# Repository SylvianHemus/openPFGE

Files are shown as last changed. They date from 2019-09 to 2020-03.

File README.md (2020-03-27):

# openPFGE

Open source and low cost pulsed-field gel electrophoresis [PFGE] equipment.
<details>
  <summary>Intro | Description | Results | Costs</summary>

## Intro
Biochemistry - including biotechnology, molecular biology, protein engineering, among others - is an area were high sophisticated equipment is required. In general, just a few equipment have an open source version - i.e. PCR - and, because of low offerer number, costs of these equipment tent to be overpriced, limiting it access to many research centers or labs.

## Description
Pulsed-field gel electrophoresis [PFGE] is a technique that allows the separation of very large DNA molecules - up to ~10 Mbp, in contrast of up to ~50 Kbp of normal electrophoresis - by a periodic change in the direction of the electric field, widely used in many biochemistry labs. This work considers the design and construction of a open source and low cost PFGE, implementing a Rotating Gel Electrophoresis (RGE). The design considers the use of a standard commercially available electrophoresis chamber and the construction of an agarose gel rotation system using 3D printed parts, a servo motor and simple electronics.

In order to keep the design simple and low cost as possible, a gel rotation system inside a standard large electrophoresis chamber was designed to achieve the electric field direction change of the PFGE. The gel rotation system considers simple 3D printed parts composed of: a tray, that supports the gel; a tray cover, that fixes the gel position; a stem, that goes from the tray cover through the electrophoresis chamber cover and joins the servo motor; and, a joint, of the stem to the servo motor that allows easy release of the tray. It also considers a 180 degrees, 5 [V], high speed and accuracy digital servo motor that allows the PFGE to move at any angle.

The buffer cooling system is composed of a small 12V pump that circulates the buffer through a peltier cooler elements based refrigeration system. A NTC epoxy thermistor temperature sensor provides the capacity to retrieve the current buffer temperature in order to feedback the cooling system.

The circuit is driven by an Arduino Nano microprocessor. It holds a serial OLED module to display the parameters of the electrophoresis run independent from the smartphone. Fans and the pump are controlled by digital outputs through high current MOSFETs. It considers a Bluetooth module to provide communication to a smartphone for system control.

## Results & costs
The equipment is capable of the separation of DNA molecules up to ~2 Mbp [See *Fig 1*] with the same protocols as commercial equipment. A 10 Mpb marker is about to be tested. It costs USD ~$500, about 1/50 of the price of commercial equipment, considering the chamber and the power source. All coding, electronics, 3D parts and documentation is public available on GitLab.
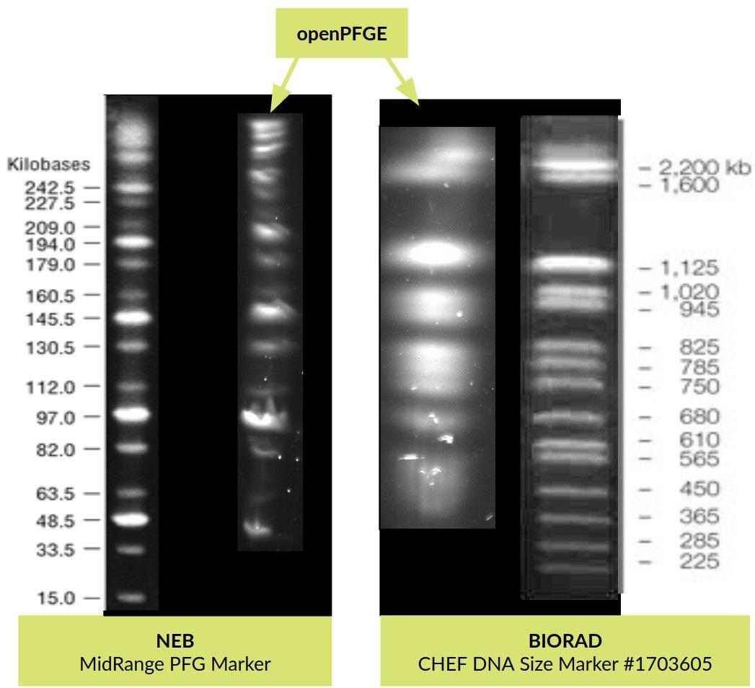
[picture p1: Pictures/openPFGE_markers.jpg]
Two commercial markers separated by openPFGE in contrast to references

**Fig. 1 |** Two commercial markers separated by openPFGE in contrast to references<br/><br/>
</details>

# Fabrication and assembly

1. Aquire all components listed in the hardware part list section
2. Print all parts in the last folder of *3D printing* folder using PLA at 0.25mm layer height, except for *pin.FCStd* that had 0.1mm layer height. See *Pictures/Gel_tray.jpg* and *Pictures/Servo_motor_support_and_join.jpg* to see how they look like in the final assembly.
3. Using some strong glue, put the magnets in the *motor joint* part as shown in *Pictures/Magnets_motor_joint.jpg* and in the *tray cover joint* part
4. Using some fishing line build the gel tray as shown in *Pictures/Gel_tray.jpg*
5. Fabricate the circuit PCB using the last version of the *fzz* file in the *Circuit* folder. You can find a good price and service at [AISLER](https://aisler.net/)
6. Assemble the circuit by soldering the parts to the PCB. The PCB has the description of the components on its skilscreen. A picture of the PCB assembly is at *Circuit/Pictures/Circuit_assembly.jpg*.
7. Assemble the servo motor to its printed support. Attach the *motor joint* to the servo arm.
8. Power the 12V power source to the circuit
9. Download [the Android app](https://play.google.com/store/apps/details?id=cl.paralelos.openpfge)
10. Turn on the circuit switch and start your electrphoresis

# Hardware parts list
## Gel rotating system
### Electrophoresis chamber
Design of motor support was made based on [BT103](https://www.btlabsystems.com/Agarose_Electrophoresis_BT103) electrophoresis chamber:

- Gel Dimension: 60 x 60, 120 x 60, 60 x 120, 120 x 120mm
- Number of samples: 6, 8, 11, 13, 18, 25
- Comb thickness: 1.0, 1.5 & 2.0mm
- Buffer volume: 650ml

### Servo
- Digital servo DS3218 [like this one](https://aliexpress.com/item/1943129663.html)
- Print 1 X *motor joint.FCStd*
- Print 1 X *motor support.FCStd*
- 4 X 3mm diameter / >10 mm length screw-nut to fix the servo to the *motor joint*
- 1 X 3mm diameter / 6 mm length screw-nut to fix the servo to the *motor support*
- 1 X 3mm diameter / 12 mm length screw-nut to fix the servo to the *motor support*
- 2 X 7mm diameter / 5 mm height N35 magnet [like this one](https://aliexpress.com/item/32277590868.html)

### Gel tray
- Print 2 X *pin.FCStd*
- Print 1 X *tray.FCStd*
- Print 1 X *tray cover.FCStd*
- Print 1 X *tray cover joint.FCStd*
- 2 X 7mm diameter / 5 mm height N35 magnet [like this one](https://aliexpress.com/item/32277590868.html)
- 30 cm fishing line

### Refigeration system
- Peristaltic Pump 12V [like this one](https://aliexpress.com/item/32882495060.html)
- Peltier cooler 12V [like this one](https://aliexpress.com/item/33028954404.html)

## Circuit parts list

### Microcontroller
Arduino Nano v3.0 ATMEGA328P [like this one](https://aliexpress.com/item/32824272738.html)

### Bluetooth
HC-05  [like this one](https://aliexpress.com/item/32953559442.html)

### Power
- L7805CV Transistor voltage regulator (1.5 A) with a heat disipator
- 100 uF capacitor
- 10 uF capacitor
- Diode 1A [like this one](https://components101.com/1n4007-diode)
- 12V / 30 A power source [like this one](https://aliexpress.com/item/32917708245.html)
- Power switch

### LCD
LCD I2C 16x2 [like this one](https://aliexpress.com/item/32786773241.html)

### Refigeration
- 1 X Epoxy NTC thermistor temperature sensor 10K 1% [like this one](https://aliexpress.com/item/32654331022.html)
- 3 X Diode 1A [like this one](https://components101.com/1n4007-diode)
- 5 X IRLB8743PBF MOSFET [like this one](https://www.infineon.com/dgdl/irlb8743pbf.pdf?fileId=5546d462533600a4015356605d6b2593)
- 6 X 10K resistor

### Input / Output
- 8 X Screw Terminal / 3.5mm / 2 pins
- 1 X Screw Terminal / 3.5mm / 3 pins

# Android APP
Available at [Google play](https://play.google.com/store/apps/details?id=cl.paralelos.openpfge).
Source code available at *App Android* folder.

# License

- Hardware license: CERN Open Hardware License 1.2
- Software license: GPL v3
- Documentation license: CC BY 4.0 International

# Open hardware certification

[OSHW] CL000001 | Certified open source hardware | [oshwa.org/cert](oshwa.org/cert)

# Thanks to
## 3D printing
[Fablab U. de Chile](http://fablab.uchile.cl/)
## App
Item picker [link](https://gist.github.com/kristopherjohnson/660656bb9e18e23146c0)
## Firmware
Thermistor code [link](https://learn.adafruit.com/thermistor/using-a-thermistor)
ArduinoJson [link](https://arduinojson.org/)
## Logo
Based on logo by [link](https://www.instagram.com/rubenferlodotcom/)

# Contact
Fell free to write about any questions to [diego.lagos.s@ug.uchile.cl](mailto:diego.lagos.s@ug.uchile.cl)

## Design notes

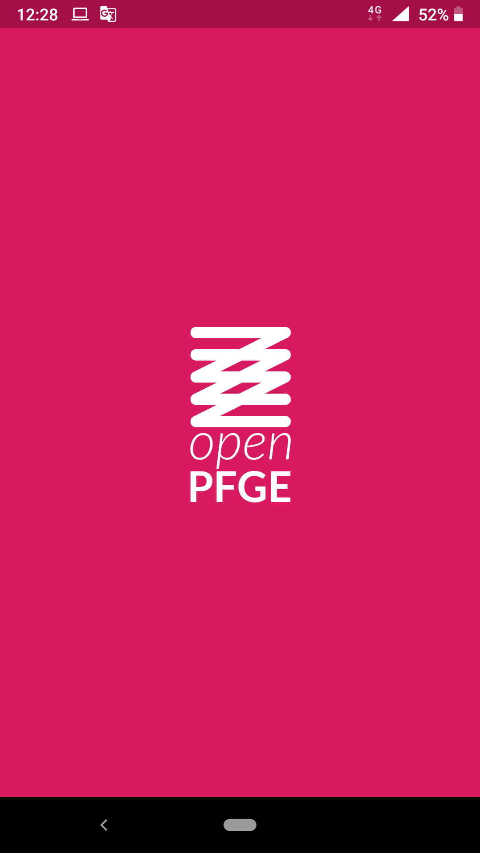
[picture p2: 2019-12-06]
App Android/Pictures/Screenshot_20191121-122839.png

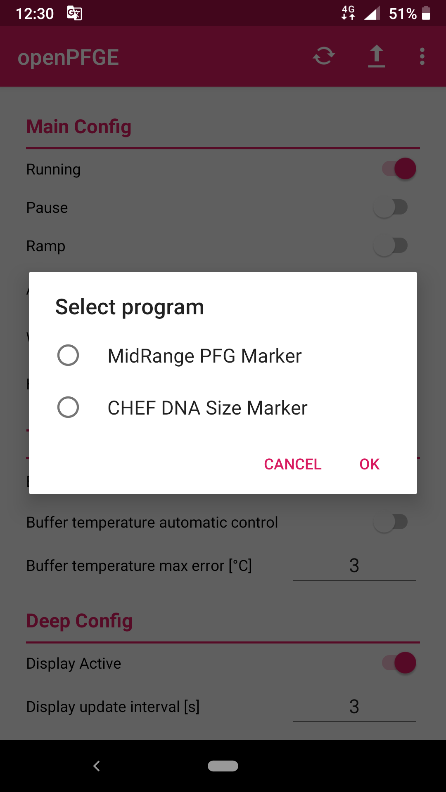
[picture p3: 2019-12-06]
App Android/Pictures/Screenshot_20191121-123048.png

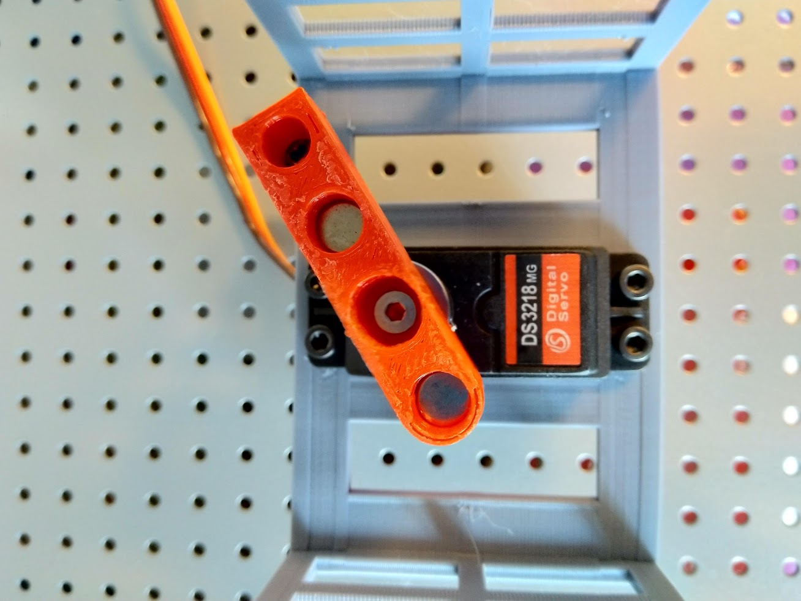
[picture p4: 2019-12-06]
Pictures/Magnets_motor_joint.jpg

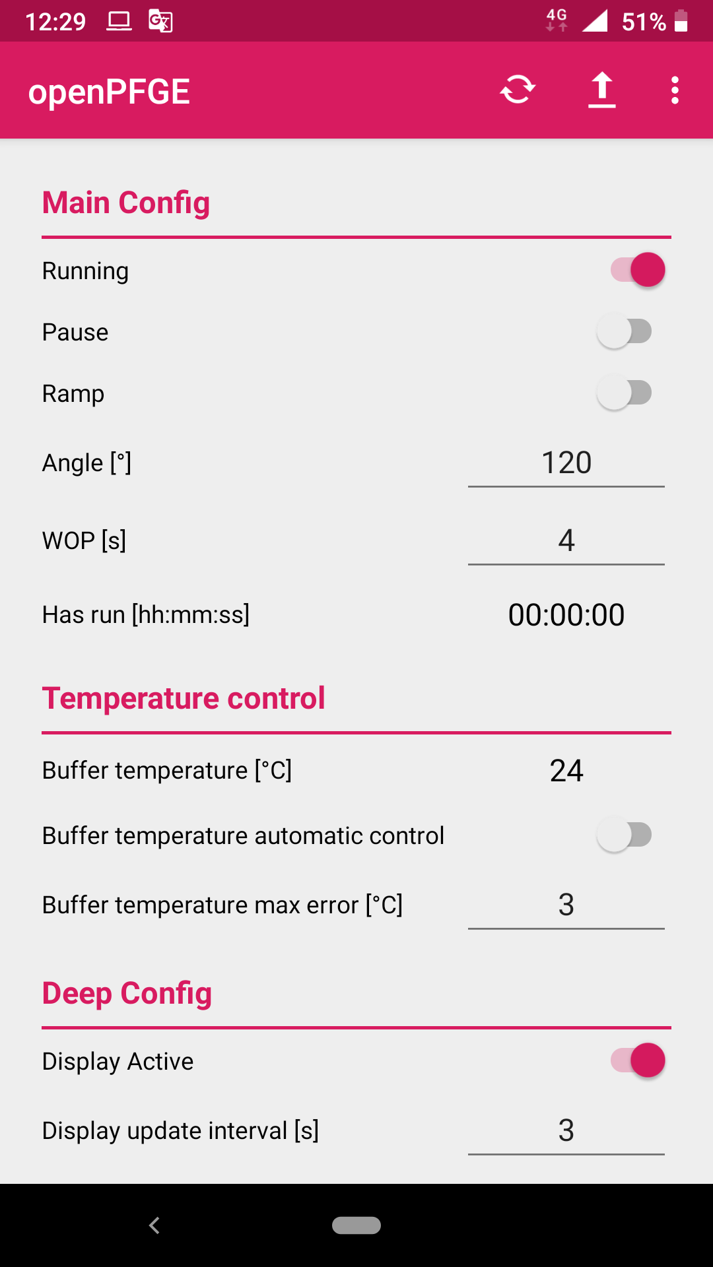
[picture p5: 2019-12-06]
App Android/Pictures/Screenshot_20191121-122949.png

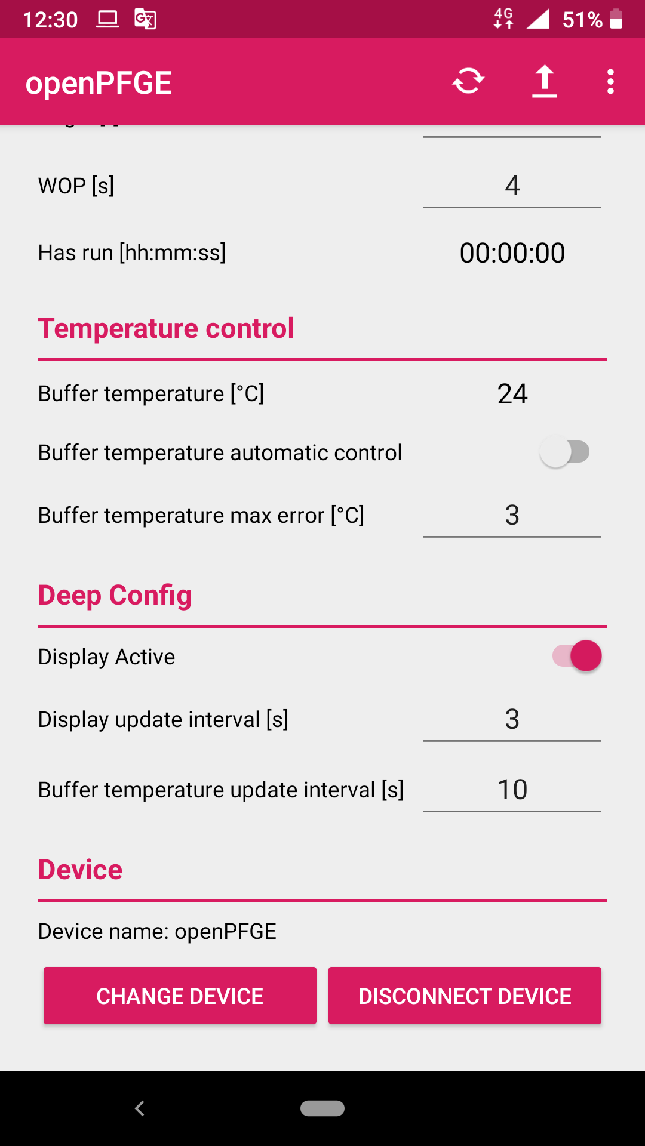
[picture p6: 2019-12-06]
App Android/Pictures/Screenshot_20191121-123005.png

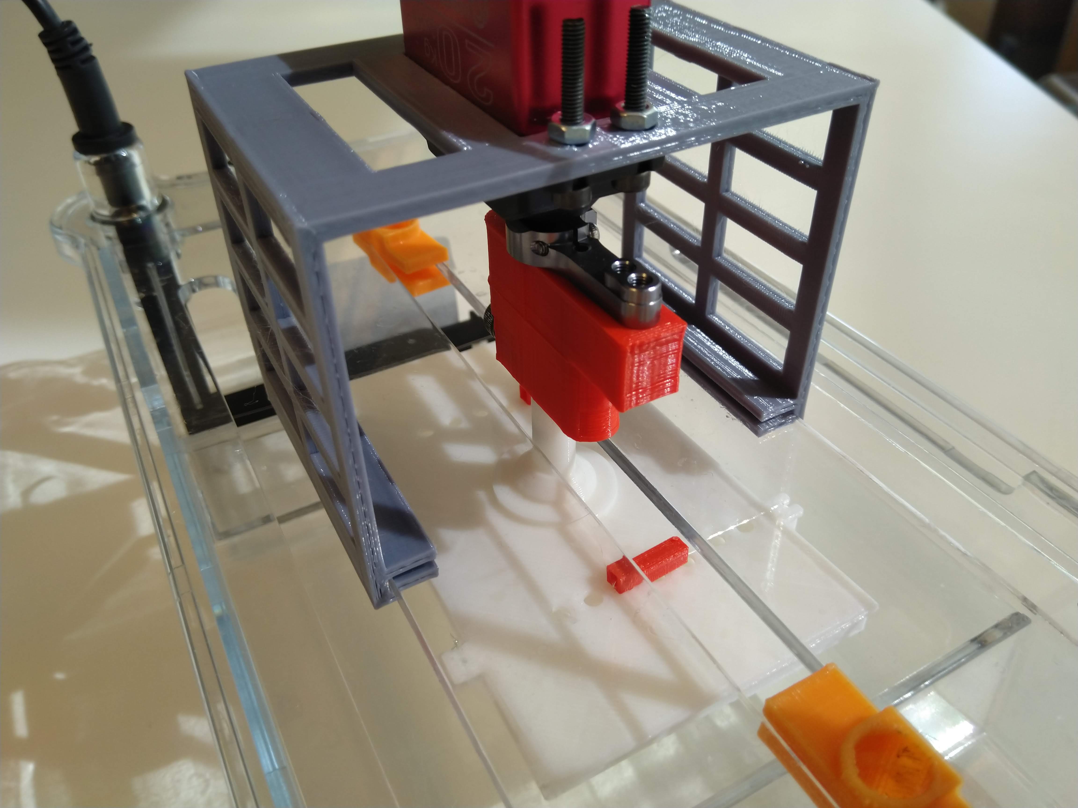
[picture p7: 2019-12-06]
Pictures/Servo_motor_support_and_join.jpg

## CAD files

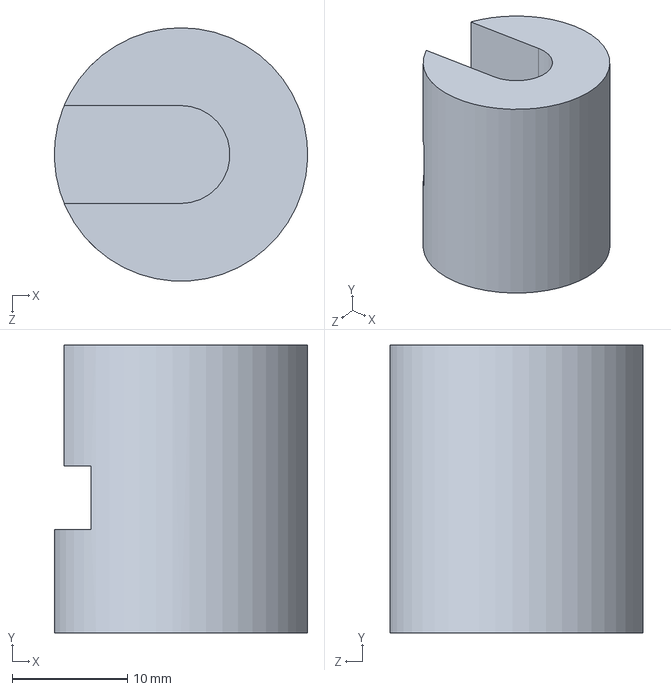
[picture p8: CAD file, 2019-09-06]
3D printing/P2.0/union cuerpo.SLDPRT
22.0 x 25.0 x 22.0 mm

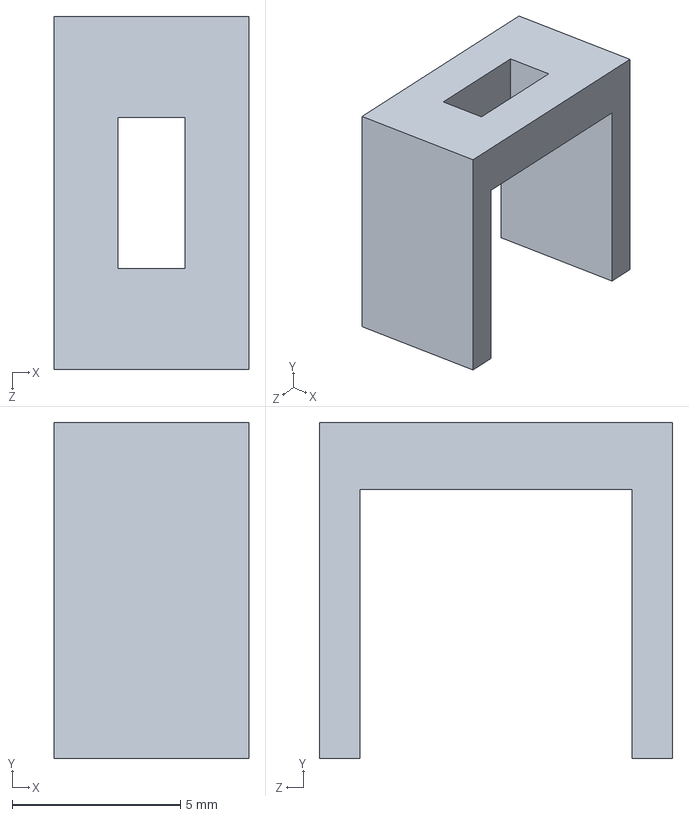
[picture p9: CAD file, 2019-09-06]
3D printing/P2.1/verticales.SLDPRT
5.80 x 10.0 x 10.5 mm

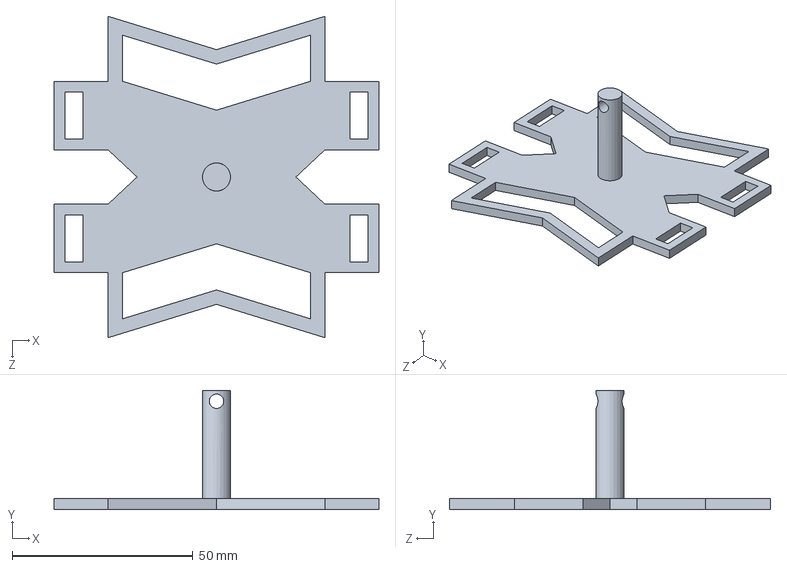
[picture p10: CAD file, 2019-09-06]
3D printing/P2.2/top larga.SLDPRT
90.0 x 33.0 x 89.0 mm

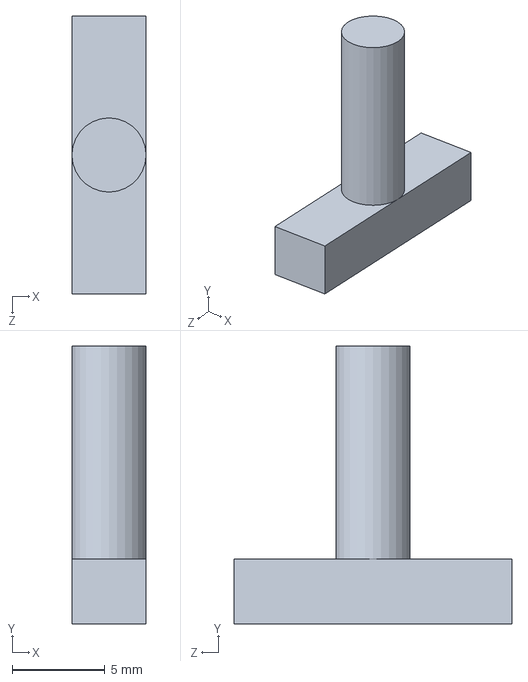
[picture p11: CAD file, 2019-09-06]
3D printing/P2.3/traba.SLDPRT
4.00 x 15.0 x 15.0 mm

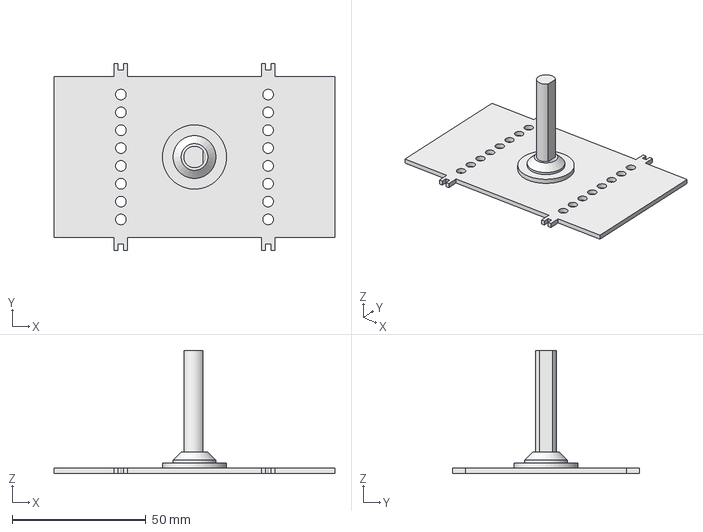
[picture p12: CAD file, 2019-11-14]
3D printing/P3.1/tray cover.FCStd
105.0 x 70.0 x 46.0 mm

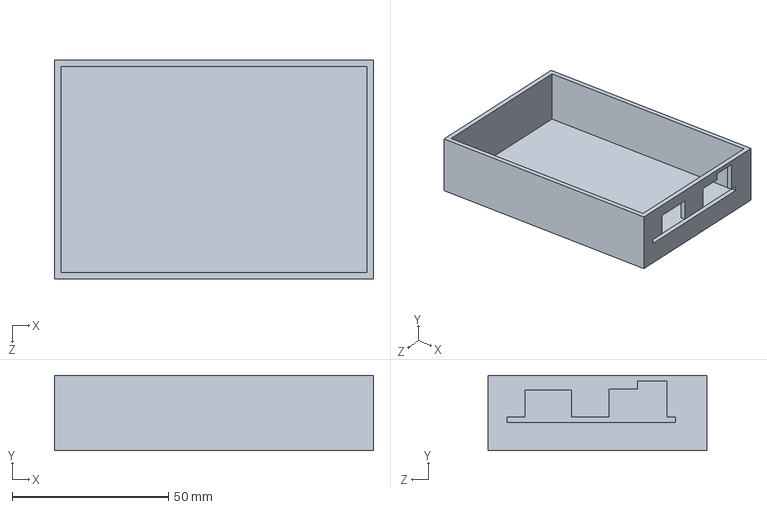
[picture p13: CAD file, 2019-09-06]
3D printing/P3/caja.SLDPRT
102.0 x 24.0 x 70.0 mm

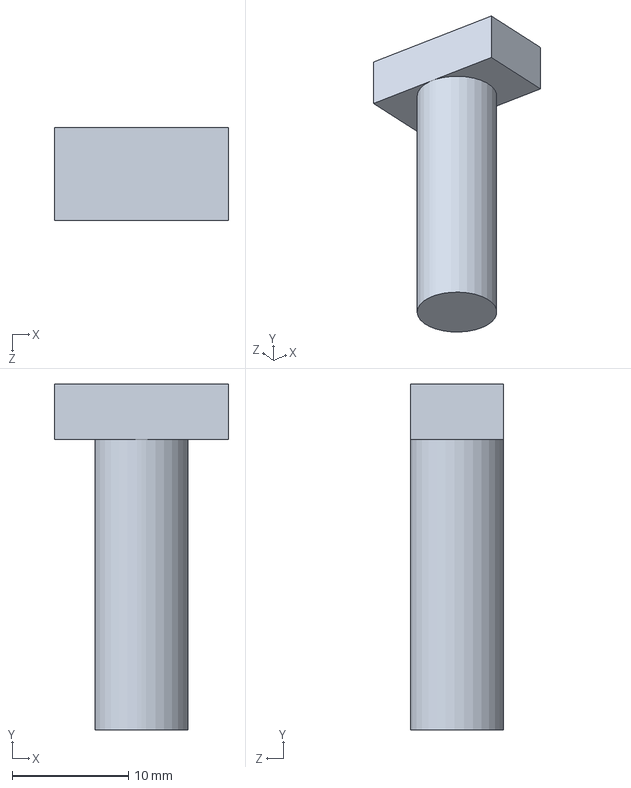
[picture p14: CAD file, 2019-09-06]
3D printing/P2.0/Union cabeza.SLDPRT
15.0 x 29.8 x 8.00 mm

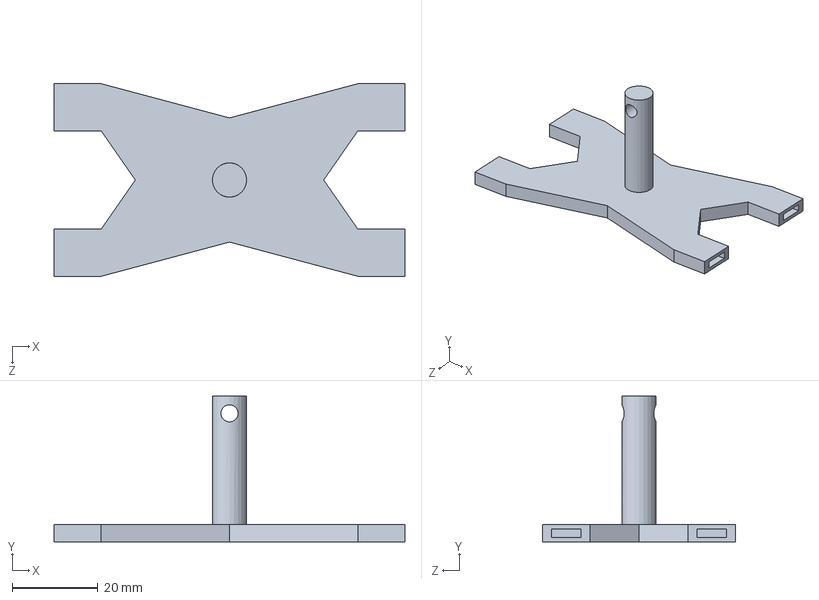
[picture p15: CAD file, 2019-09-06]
3D printing/P2.1/top.SLDPRT
82.0 x 34.0 x 45.0 mm

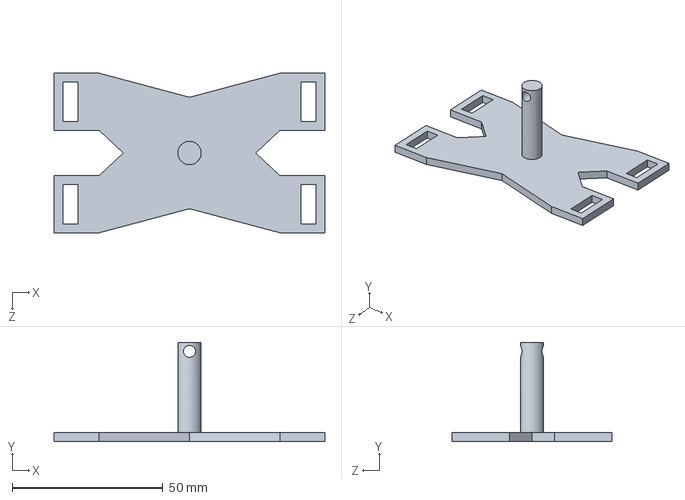
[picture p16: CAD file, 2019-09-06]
3D printing/P2.2/top.SLDPRT
90.0 x 33.0 x 53.0 mm

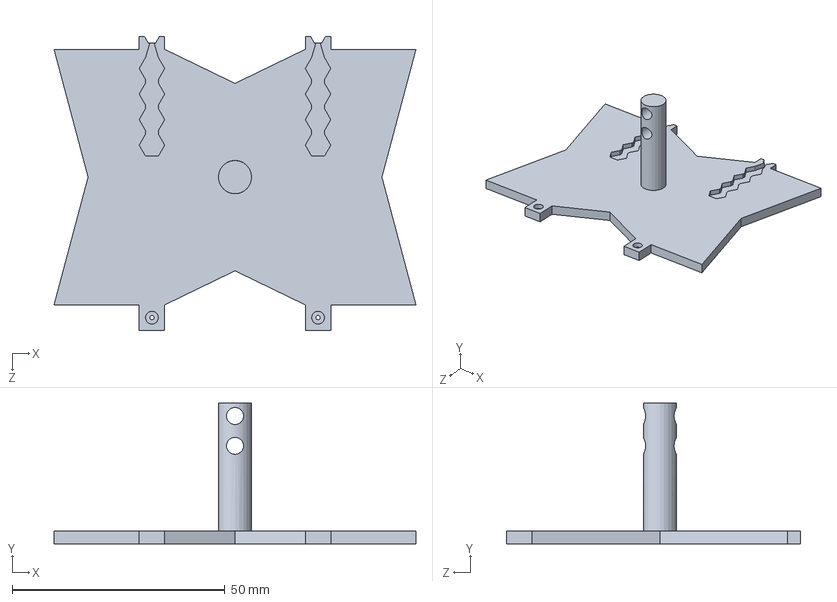
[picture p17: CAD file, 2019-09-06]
3D printing/P2.3/top larga.SLDPRT
85.0 x 33.0 x 69.0 mm

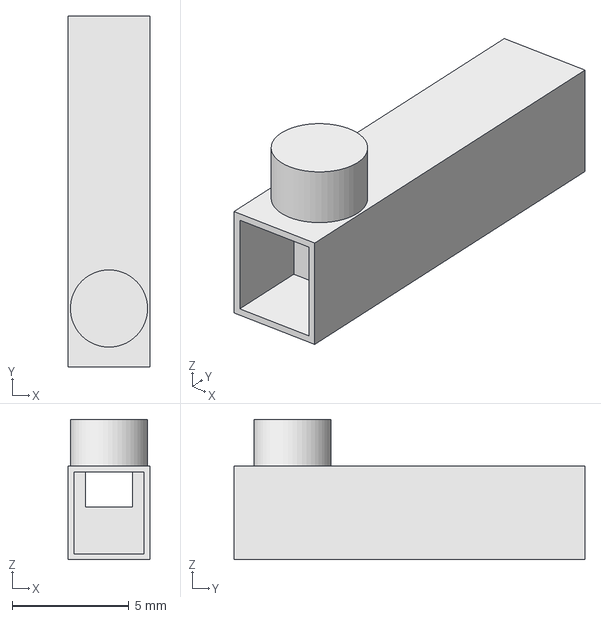
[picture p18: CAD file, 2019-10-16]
3D printing/P3.1/pin.FCStd
3.50 x 15.0 x 6.00 mm

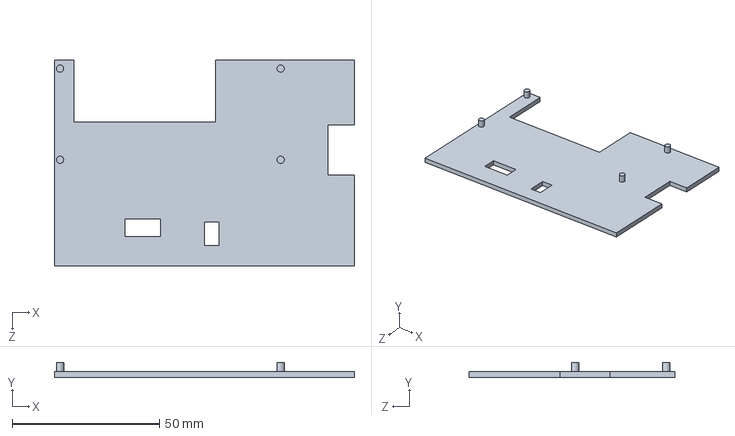
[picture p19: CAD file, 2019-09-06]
3D printing/P3/caja top.SLDPRT
102.0 x 5.00 x 70.0 mm

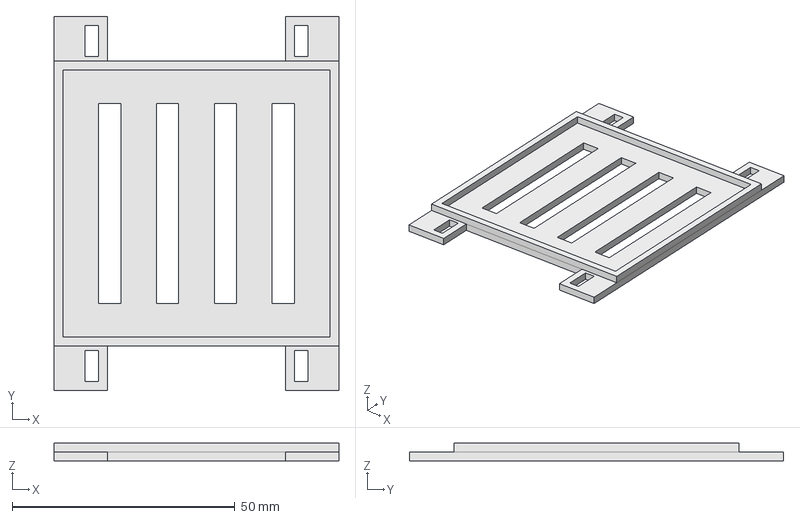
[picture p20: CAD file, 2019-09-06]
3D printing/P2.0/bottom V2.FCStd
64.0 x 84.0 x 4.00 mm

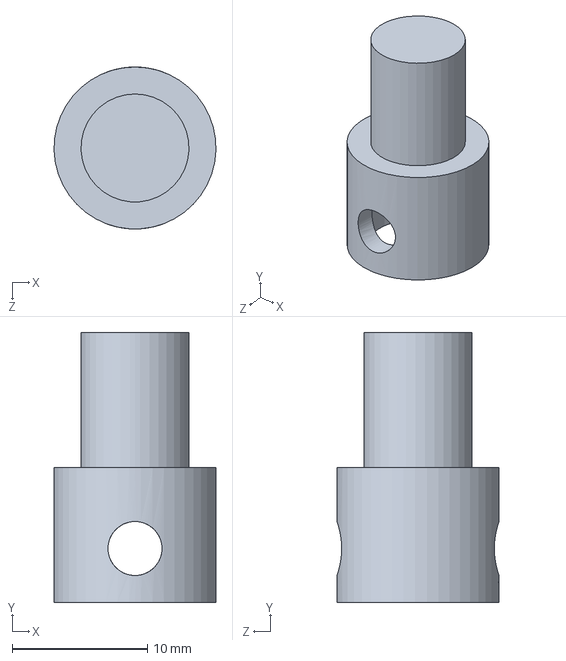
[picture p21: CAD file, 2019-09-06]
3D printing/P2.1/union motor.SLDPRT
12.0 x 20.0 x 12.0 mm

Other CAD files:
3D printing/P2.2/base.SLDPRT
3D printing/P2.3/base larga.SLDPRT
3D printing/P3.1/tray.FCStd
3D printing/P2.0/pin V3.SLDPRT
3D printing/P2.0/top V2.FCStd
3D printing/P2.1/base larga.SLDPRT
3D printing/P2.1/base.SLDPRT
3D printing/P2.2/base larga.SLDPRT
3D printing/P2.2/fix.SLDPRT
3D printing/P2.3/agarre.SLDPRT
3D printing/P3.1/hose_adapter.SLDPRT
3D printing/P3.1/hose_adapter.stl
3D printing/P3.1/motor joint.FCStd
3D printing/P3.1/motor support.FCStd
3D printing/P3.1/tray cover joint.FCStd
3D printing/P3/base.f3d
3D printing/P3/motor join.f3d
3D printing/P3/top.f3d

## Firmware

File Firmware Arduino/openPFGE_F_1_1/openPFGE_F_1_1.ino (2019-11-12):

// connections
// servo: Pin 9 (& 5v (4.8 - 7.2 V) to power source)
// thermoresistor: GND and A0 (& 10 kohm from Pin A0 to 3.3V && wire 3.3V with AREF on arduino)
// bluetooth hc-05: RX --> Pin 11 & TX --> Pin 10 (& 5v to power source)
// LCD/I2C VCC -> 5V / GND -> GND / SDA -> A4 / SCL -> A5
// Mosfet Pump --> Pin 3
// Mosfet Fan 1 --> Pin 5
// Mosfet Fan 2 --> Pin 6
// Mosfet Peltier 1 --> Pin 7
// Mosfet Peltier 2 --> Pin 8

// libraries
#include <SoftwareSerial.h>
#include <Chrono.h>
#include <VarSpeedServo.h>
#include <Wire.h>
#include <LiquidCrystal_I2C.h>

// firmware
#define firmwareVersion 1
#define firmwareSubversion 0

// debug
#define serialDebug false // should the program outputs the debug by serial port
bool serialStarted = false; // serial started?

// motor servo
VarSpeedServo servo; // the servo object
#define servoPin 9 // PWM signal pin
#define servoUsFrom 500 // minimum microseconds // for ds3218
#define servoUsTo 2500 // maximum microseconds // for ds3218
#define servoVelocity 50 // 0=full speed, 1-255 slower to faster
#define waitForMotorMove true // programs wait until motor end moving
int motorPosition = 0; // store current motor position (-1 = left, 0 = center, 1 = right)

// bluetooth
SoftwareSerial BT(10, 11); // TX, RX

// LCD / I2C
LiquidCrystal_I2C lcd(0x27, 16, 2); // Direction 0x27 & 16 cols & 2 rows
Chrono lcdTimer(Chrono::SECONDS); // Chrono for info update and view change
bool lcdActive = true; // update lcd info?
bool lcdView = 0; // lcd info is shown in diferent views. This holds the current view
bool lcdBacklight = false; // backlight on/off
int lcdUpdateInfoInterval = 2; // lcd update info interval (seconds)

// temperature control
int bufferTemperature = 0; // current read of buffer temperature
bool bufferTemperatureAutomaticControl = false; // if temperature of the buffer is automaticlly controlled by the refrigeration system
bool bufferCoolingOn = false;
int bufferTemperatureSetpoint = 15; // optimal buffer temperature (°C)
int bufferTemperatureMaxError = 3; // max diference between current buffer temperature and set point allowed before start the cooling system
#define bufferTemperatureSetpointMin 10
#define bufferTemperatureSetpointMax 30
#define bufferTemperatureMaxErrorMin 1
#define bufferTemperatureMaxErrorMax 10
#define pumpPin 3
#define fan1Pin 5
#define fan2Pin 6
#define peltier1Pin 7
#define peltier2Pin 8

// running parameters
bool onoff = false; // System on/off
bool pause = false; // System paused on/off
bool ramp = false; // System ramp on/off
int angle = 120; // Turning angle
int wop = 4; // between each movement in ramp off mode (seconds)
int wopAuto = 0; // // between each movement in ramp on mode (seconds)
#define maxWop 1000 // max wop value for ramp start/end (seconds)
#define maxRampDuration 100 // ramp max duration (hours)
int rampStart = 1; // initial time movement in ramp on mode (seconds)
int rampEnd = 25; // final time movement in ramp on mode (seconds)
int rampDuration = 24; // ramp time in ramp on mode (hours)

// variables
String inData; // capture serial inputs
String method; // switch commands from serial input
#define tmpBufferSize 100
char tmpBuffer[tmpBufferSize]; // temporal
bool autoEnd = false; // whether the program has automaticlly ended
#define maxIntervalUpdate 60 // 60 seconds for maximum update interval
int bufferTemperatureUpdateInterval = 10; // buffer temperature update interval (seconds)
#define methodSync "y"
#define methodSet "s"
#define methodWho "w"
#define methodAutomaticEnd "a"
#define methodUnknown "u"

// timers
Chrono runTimer(Chrono::SECONDS); // running timer
Chrono stepTimer(Chrono::SECONDS); // step timer
Chrono bufferTemperatureTimer(Chrono::SECONDS); // buffer temperature update timer

void setup() {
  // Chronos
  runTimer.stop();
  stepTimer.stop();
  bufferTemperatureTimer.stop();
  lcdTimer.stop();

  // LCD
  lcd.init();
  lcd.noBacklight();

  // Motor init and center
  centerMotor();

  // thermoresistor
  analogReference(EXTERNAL); // Connect AREF to 3.3V!

  // temperature control
  pinMode(pumpPin, OUTPUT);
  pinMode(fan1Pin, OUTPUT);
  pinMode(fan2Pin, OUTPUT);
  pinMode(peltier1Pin, OUTPUT);
  pinMode(peltier2Pin, OUTPUT);
  digitalWrite(pumpPin, LOW);
  digitalWrite(fan1Pin, LOW);
  digitalWrite(fan2Pin, LOW);
  digitalWrite(peltier1Pin, LOW);
  digitalWrite(peltier2Pin, LOW);

  // BT series port initialice (For Mode AT 2)
  BT.begin(9600);

  // debug
  serialDebugWrite("Setup done");
}

void loop() {
  // Check whether is there anything at serial
  loopSerial();

  // Make the next motor move
  loopMotor();

  // buffer temperature loop
  loopBufferTemperature();

  // lcd loop
  loopLcd();
}

void loopSerial() {
  if (BT.available())
  {
    inData = requestString();
    //serialDebugWrite("inData | " + inData);

    strcpy(tmpBuffer, inData.c_str());

    strtok(strtok(tmpBuffer, "@"), "=");
    method = strtok(NULL, "=");

    //serialDebugWrite("method | " + method);

    if (method == methodWho) {
      sprintf(tmpBuffer, "m=%s@fv=%d@fs=%d", methodWho, firmwareVersion, firmwareSubversion);
      btSendMessage(tmpBuffer);
    } else if (method == methodSync) {
      encodeCurrent();
      sprintf(tmpBuffer + strlen(tmpBuffer), "@m=%s", methodSync);
      btSendMessage(tmpBuffer);
    } else if (method == methodAutomaticEnd) {
      sprintf(tmpBuffer, "m=%s", methodAutomaticEnd);
      btSendMessage(tmpBuffer);
    } else if (method == methodSet) {
      setParams();
      encodeCurrent();
      sprintf(tmpBuffer + strlen(tmpBuffer), "@m=%s", methodSet);
      btSendMessage(tmpBuffer);
    } else {
      sprintf(tmpBuffer, "m=%s", methodUnknown);
      btSendMessage(tmpBuffer);
    }
  }
}

void setParams() {
  strcpy(tmpBuffer, inData.c_str());
  char * pch;
  char * pchv;
  pch = strtok(tmpBuffer, "@=");
  while (pch != NULL)
  {
    pchv = strtok(NULL, "@=");
    if (strcmp(pch, "o") == 0) {
      setOnOff(stob(pchv));
    } else if (strcmp(pch, "p") == 0) {
      setPause(stob(pchv));
    } else if (strcmp(pch, "r") == 0) {
      setRamp(stob(pchv));
    } else if (strcmp(pch, "a") == 0) {
      angle = constrain(stoi(pchv), 1, 180);
    } else if (strcmp(pch, "w") == 0) {
      wop = constrain(stoi(pchv), 1, maxWop);
    } else if (strcmp(pch, "rs") == 0) {
      rampStart = constrain(stoi(pchv), 1, rampEnd - 1);
    } else if (strcmp(pch, "re") == 0) {
      rampEnd = constrain(stoi(pchv), rampStart + 1, maxWop);
    } else if (strcmp(pch, "rd") == 0) {
      rampDuration = constrain(stoi(pchv), 1, maxRampDuration);
    } else if (strcmp(pch, "ae") == 0) {
      autoEnd = false; // set to false always if it is set
    } else if (strcmp(pch, "la") == 0) {
      lcdActive = stob(pchv);
    } else if (strcmp(pch, "lb") == 0) {
      lcdBacklight = stob(pchv);
    } else if (strcmp(pch, "lui") == 0) {
      lcdUpdateInfoInterval = constrain(stoi(pchv), 1, maxIntervalUpdate);
    } else if (strcmp(pch, "bui") == 0) {
      bufferTemperatureUpdateInterval = constrain(stoi(pchv), 1, maxIntervalUpdate);
    } else if (strcmp(pch, "btac") == 0) {
      bufferTemperatureAutomaticControl = stob(pchv);
    } else if (strcmp(pch, "bts") == 0) {
      bufferTemperatureSetpoint = constrain(stoi(pchv), bufferTemperatureSetpointMin, bufferTemperatureSetpointMax);
    } else if (strcmp(pch, "btm") == 0) {
      bufferTemperatureMaxError = constrain(stoi(pchv), bufferTemperatureMaxErrorMin, bufferTemperatureMaxErrorMax);
    }
    pch = strtok(NULL, "@=");
  }
}

void loopMotor() {
  if (onoff && !pause) {
    nextMotorMove();
  }
}

void nextMotorMove() {
  int currentwop = wop;
  if (ramp) {
    currentwop = wopAuto;
  }
  if (runTimer.isRunning() && stepTimer.elapsed() > currentwop) {
    if (motorPosition == 0 || motorPosition == -1) {
      // go to +1 position
      moveMotor((int) (90.0 + angle / 2.0));
      motorPosition = 1;
    } else {
      // go to -1 position
      moveMotor((int) (90.0 - angle / 2.0));
      motorPosition = -1;
    }
    setNextWopAuto();
    stepTimer.restart();
  }
}

void setNextWopAuto() {
  if (ramp) {
    if (runTimer.hasPassed((long) rampDuration * 3600)) {
      // Run end time reached
      centerMotor();
      runTimer.stop();
      //serialDebugWrite("Automatic System Off [Run end time reached]");
      autoEnd = true;
    } else {
      wopAuto = map((long) runTimer.elapsed(), (long) 0, (long) rampDuration * 3600, (long) rampStart, (long) (rampEnd + 1)); // +1 to be able to reach the last ramp wop
    }
  }
}

void centerMotor() {
  moveMotor(90);
  motorPosition = 0;
}

void moveMotor(int finalAngle) {
  servo.attach(servoPin);
  delay(15);
  //servo.writeMicroseconds(map(finalAngle, 0, 180, servoUsFrom, servoUsTo));
  servo.write(map(finalAngle, 0, 180, servoUsFrom, servoUsTo), servoVelocity, waitForMotorMove);
  servo.detach();
}

void loopLcd() {
  if (!lcdTimer.isRunning() || lcdTimer.hasPassed(lcdUpdateInfoInterval)) {
    if (lcdActive) {
      lcd.clear();
      if (lcdBacklight) {
        lcd.backlight();
      } else {
        lcd.noBacklight();
      }
      if (autoEnd) {
        lcd.print("AUTO END");
        // Has run
        lcd.setCursor(0, 1);
        lcd.print(secondsToTime(runTimer.elapsed()));
      } else {
        if (lcdView == 0) {
          // OnOff
          if (onoff) {
            if (pause) {
              lcd.print("Pause");
            } else {
              lcd.print("On");
            }
          } else {
            lcd.print("Off");
          }
          // Has run
          lcd.setCursor(8, 0);
          lcd.print(secondsToTime(runTimer.elapsed()));
          // Ramp
          lcd.setCursor(0, 1);
          lcd.print("Ramp/");
          if (ramp) {
            lcd.print("On");
          } else {
            lcd.print("Off");
          }
          // Angle
          lcd.setCursor(9, 1);
          lcd.print("Ang/");
          lcd.print(angle);

          lcdView = 1;
        } else if (lcdView == 1) {
          // Buffer temperature
          lcd.print("BT/");
          lcd.print(bufferTemperature);
          lcd.setCursor(8, 0);
          lcd.print("WOP/");
          if (ramp) {
            lcd.print(wopAuto);
            lcd.setCursor(0, 1);
            lcd.print("S/");
            lcd.print(rampStart);
            lcd.print(" E/");
            lcd.print(rampEnd);
            lcd.print(" D/");
            lcd.print(rampDuration);
          } else {
            lcd.print(wop);
          }

          lcdView = 0;
        }
      }
      lcdTimer.restart();
    } else {
      lcd.clear();
      lcd.noBacklight();
    }
  }
}

void loopBufferTemperature() {
  if (!bufferTemperatureTimer.isRunning() || bufferTemperatureTimer.hasPassed(bufferTemperatureUpdateInterval)) {
    bufferTemperature = readTemperature();
    bufferTemperatureTimer.restart();
  }

  if(bufferTemperatureAutomaticControl){
    // decide if cooling is needed
    if (bufferTemperature + bufferTemperatureMaxError > bufferTemperatureSetpoint && !bufferCoolingOn) { // start cooling
      digitalWrite(pumpPin, HIGH);
      digitalWrite(fan1Pin, HIGH);
      digitalWrite(fan2Pin, HIGH);
      digitalWrite(peltier1Pin, HIGH);
      digitalWrite(peltier2Pin, HIGH);
      bufferCoolingOn = true;
    } else { // stop cooling
      if (bufferCoolingOn) { // just if it is cooling
        digitalWrite(pumpPin, LOW);
        digitalWrite(fan1Pin, LOW);
        digitalWrite(fan2Pin, LOW);
        digitalWrite(peltier1Pin, LOW);
        digitalWrite(peltier2Pin, LOW);
        bufferCoolingOn = false;
      }
    }
  }
}

void setOnOff(bool newOnOff) {
  if (onoff == newOnOff) {
    //serialDebugWrite("setOnOff | Already in the state ");
    return;
  }
  if (newOnOff) {
    runTimer.restart();
    stepTimer.restart();
    setNextWopAuto();
    autoEnd = false;
  } else {
    runTimer.stop();
    stepTimer.stop();
    centerMotor();
  }
  onoff = newOnOff;
}
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

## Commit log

2019-09-06 From Drive to GitLab
    [Union cabeza.SLDPRT, agarre.SLDPRT, base larga.SLDPRT, base.SLDPRT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]
2019-09-06 Circuit update
    [openPFGE H1.0.fzz]
2019-09-09 Replace openPFGE H1.0.fzz
    [openPFGE H1.0.fzz]
2019-09-10 Project structure and Circuit Update
    [Union cabeza.SLDPRT, agarre.SLDPRT, base larga.SLDPRT, base.SLDPRT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]
2019-09-11 Circuit and app updates
    [openPFGE H1.0.fzz, openPFGE H1.1.fzz, top joint.FCStd]
2019-09-13 Circuit, firmware and app updates
2019-09-13 3D updates
    [motor joint.FCStd, top joint.FCStd]
2019-09-25 App, Logo & Firmware updates
    [openPFGE H1.1.fzz]
2019-09-25 Circuit H1.2
    [openPFGE H1.2.fzz]
2019-09-25 Circuit H1.1 restore
    [openPFGE H1.1.fzz]
2019-09-25 Circuit H1.2 update (autorouting)
    [openPFGE H1.2.fzz]
2019-09-26 Firmware & circuit updates
    [openPFGE H1.2.fzz]
2019-10-02 Arduino 12V power
    [openPFGE H1.2.fzz]
2019-10-03 Adding buffer temperature max error support
2019-10-11 3D minor adjust
    [cover joint.FCStd, motor joint.FCStd]
2019-10-16 pin update
    [pin.FCStd]
2019-10-16 Circuit H1.2 autorouting
    [openPFGE H1.2.fzz]
2019-10-16 H1.2 minor updates
    [openPFGE H1.2.fzz]
2019-10-30 Circuit minor updates
    [openPFGE H1.2.fzz]
2019-10-30 Circuit & ATMODE code minor updates
    [openPFGE H1.2.fzz]
2019-11-07 small updates
    [openPFGE H1.2.fzz, openPFGE H1.3.fzz]
2019-11-11 Minor updates
    [openPFGE H1.3.fzz]
2019-12-12 oshwa cert
    [openPFGE H1.3.fzz]
2020-06-26 Buffer temperature control update
2020-07-08 Servo microseconds update
2022-04-29 Hose adapter uploads
    [hose_adapter.SLDPRT, hose_adapter.stl]
